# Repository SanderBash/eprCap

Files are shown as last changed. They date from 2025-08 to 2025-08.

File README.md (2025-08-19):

# eprCap
## Description
Design files and description to build a simple flowthrough EPR capillary sample chamber that fits 8 mm collets.

eprCap is meant to enable researchers to build a simple and reliable capillary sample system for aqeous or lossy EPR samples. It is based on a 3D printed cap, that holds an inner glass capillary of 1 mm outer diameter and a protective outer tube, e.g. a recycled 4 mm quartz tube. The assembly is held together with expoxy glue.

## BOM
 - 2x EPR Capillary Glue Ferrules
 - 1x 4 mm OD quartz or glass tube
 - 1x 1 mm OD glass capillary
 - 2x 1/16" OD, 1/32" ID PTFE tubing of desired length
 - 1x Blunt needle (21G size)

## Build instructions
### Outer casing
1. Print the EPR Capillary Glue Ferrule two times.
2. Determine the length of the outer 4 mm glass or quartz tube that is needed to fit in your resonator, making sure the printed parts fit into the top and bottom collet.
3. Cut the outer tube to length.
4. Mix up some 5 minute epoxy and fill the outer tube recess in both ferrules.
5. Insert the tube into the ferrules and align the assembly on a flat surface, along a straight edge (see picture, aluminum ruler) and let dry.

<p align="center">
 
</p>

### Inner capillary assembly
6. Cut the 1 mm OD glass capillary to desired length, such that it does not protrude outside of the 3D printed ferrules, to prevent breakage.
7. Use a heat gun or small torch to soften the ends of the two pieces of tubing (i.e. 1/16" OD, 1/32" ID) and slide them over the 1 mm OD capillary. Upon cooling, they will be a shrink fit and suitable for low pressure operation.
8. Feed the tubing and capillary into the outer casing.
9. Mix up a new batch of 5 minute epoxy and glue the tubing/capillary assembly into the ferrules. You can add some epoxy at both ends and slide the tubing back and forth to work the glue into the ferrule hole.

<p align="center">
 
</p>

10. Heat up one of the tubing ends to soften it and push it onto a blunt needle. See the finished result below.

<p align="center">
 
 <p/>

## Usage
Feed the tubing through the resonator and clamp the top and bottom ferrule using the resonator's collets, see image below. Fill the capillary using a syringe and record some spectra.

<p align="center">
 
 <p/>

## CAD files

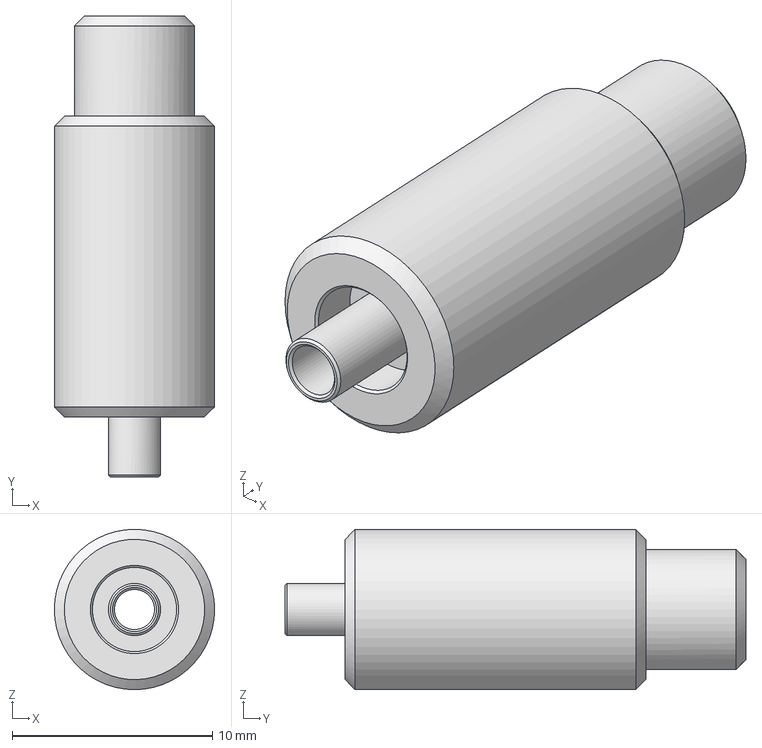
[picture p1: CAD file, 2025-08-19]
Design Files/EPR Capillary Glue Ferrule.stp
8.00 x 23.0 x 8.00 mm

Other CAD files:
Design Files/EPR Capillary Glue Ferrule.ipt
Design Files/EPR Capillary Glue Ferrule.stl

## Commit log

2025-08-19 Rename EPR Capillary Glue Ferrule.ipt to Design Files/EPR Capillary Glue Ferrule.ipt
    Moved to folder
    [EPR Capillary Glue Ferrule.ipt]
2025-08-19 Rename EPR Capillary Glue Ferrule.stl to Design Files/EPR Capillary Glue Ferrule.stl
    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
    [EPR Capillary Glue Ferrule.stl]
2025-08-19 Update README.md
    Added images, changed 5 mm to 4 mm (typo)
2025-08-19 Create EPR Capillary Glue Ferrule.stp
    Added .step file
    [EPR Capillary Glue Ferrule.stp]
2025-08-19 Add files via upload
    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
    [EPR Capillary Glue Ferrule.stp]
